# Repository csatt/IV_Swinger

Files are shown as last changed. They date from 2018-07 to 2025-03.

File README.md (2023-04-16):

# IV_Swinger

**NOTICE: Please contact me at csatt1@gmail.com if you are interested in building the hardware for people who don't have the time, skills, or tools to do it themselves. I get requests occasionally from such people, but cannot do this myself. There are now PCBs, making the construction much easier!**

The IV Swinger is an IV curve tracer for photovoltaic solar panels. Both the hardware design and the software are open source.

This GitHub repository contains the IV Swinger documentation, software, and open source licensing files.

IV Swinger 2 is here! It is much smaller, cheaper and easier to build, and better than the original in almost every way. Step-by-step construction instructions are included in the repository, and are posted on www.instructables.com:

[IV Swinger 2 - a $50 IV Curve Tracer](http://www.instructables.com/id/IV-Swinger-2-a-50-IV-Curve-Tracer/)

All IV Swinger 2 documentation is now available:
* IV Swinger 2: User Guide
* IV Swinger 2: Optional Environmental Sensors
* IV Swinger 2: Hardware Scaling
* IV Swinger 2: Design and Theory of Operation
* IV Swinger 2: Step-by-step Construction (for each variant)
* Fritzing files
* PCB schematics
* Bills of materials (BOMs) for each variant

YouTube demo videos (IV Swinger 2):

IV Swinger 2 Demo: Part I (http://www.youtube.com/watch?v=WhnTWciiNNo)

IV Swinger 2 Demo: Part II (http://www.youtube.com/watch?v=9iPq5AsuU_U)

YouTube demo video (original IV Swinger):

IV Swinger Demo (http://www.youtube.com/watch?v=xNytkONOcW0)

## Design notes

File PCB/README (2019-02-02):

This folder contains subfolders for each different type of IV Swinger
PCB.  Each subfolder contains an EAGLE subfolder with the schematic and
board files created with the free version of EAGLE.  There is also a
Gerber subfolder with the manufacturing files (in a zip archive) and a
PDF subfolder with PDFs of the schematic and images of the top and
bottom of the PCB.

All PCBs are Arduino "shields" that replace the PermaProto board in the
original IV Swinger 2 design.  They plug onto the top of the Arduino.
All are 2-layer boards.

IV_Swinger_2_module
-------------------
  This is the version for PV modules that requires an external
  electromechanical relay (EMR) module, just like the original. The only
  external wiring is between one screw-terminal block on the PCB and the
  relay module and between another screw-terminal block and the binding
  posts.  Additional external wires are required for the optional
  temperature and irradiance sensors.

  RevB
  ----
  Based on RevB of the SSR-based module version. The main purpose of
  this revision is to make the SSR and EMR versions as similar as
  possible, namely:

     - the connections to the binding posts are both on a screw-terminal
       block on the left end of the board (like SSR version)

     - pads are provided for the bypass diodes (like SSR version)

     - the current-carrying path from the shunt is now isolated in a
       stub off the ground plane (like SSR version)

     - R3 is now connected to the shunt with a dedicated trace (like SSR
       version)

     - Connections to EMR are from a second screw-terminal block that is
       located on the board where the SSRs are in the SSR version

  Note that there is nothing "wrong", per se, with the RevA board. This
  just cleans a few things up and makes it much easier to compare it
  with the SSR version.
  
  Status:   Verified
  To order: Submit Gerber files to www.pcbway.com

  RevA
  ----
  Status: OBSOLETE (but bug-free)

IV_Swinger_2_cell
-----------------
  This is similar to the IV_Swinger_2_module Arduino shield, but it is
  for use with PV cells.

  RevA
  ----
  Status:   Verified
  To order: Submit Gerber files to www.pcbway.com

IV_Swinger_2_ss_mod
-------------------
  This is similar to the IV_Swinger_2_module Arduino shield, but it uses
  three solid-state relays (SSRs) instead of the one electromechanical
  relay (EMR) module.  The only off-board connections are to the PV
  module itself (PV- and PV+). These can go to binding posts, or can be
  connected directly to wires with MC-4 connectors on their ends.

  RevB
  ----
  Status: Verified

  To order: Submit Gerber files to www.pcbway.com

  RevA
  ----
  Status: OBSOLETE (bugs: Issue #40, Issue #41; not viable)

IV_Swinger_2_ss_cell
--------------------
  This is similar to the IV_Swinger_2_ss_mod Arduino shield, but it is
  for use with PV cells.  It requires four SSRs.

  RevB
  ----
  Status:   Verified
  To order: Submit Gerber files to www.pcbway.com

  RevA
  ----
  Status:   OBSOLETE (bug: Issue #49, rework possible)

--------------------------------------------------------------------------------

Advantages of EMR designs:
  - EMR module is inexpensive (~$2), vs three/four SSRs (~$21/$28)
  - "Clicks" tell you it's working
  - EMR module is easy to replace if it goes bad
  
Advantages of SSR designs:
  - On-board:
     - No wires
     - No relay module to mount
  - Rated at 100V
  - No mechanical wearout
  - Silent

NOTE: The IV Swinger 2 Arduino code and application software work with
      all four variants.

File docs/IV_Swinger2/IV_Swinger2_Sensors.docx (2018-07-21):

# IV Swinger 2

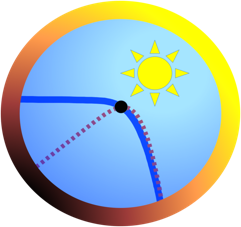
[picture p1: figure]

Optional Environmental Sensors

Document Revision: 1.00 (20-Jul, 2018) Chris Satterlee

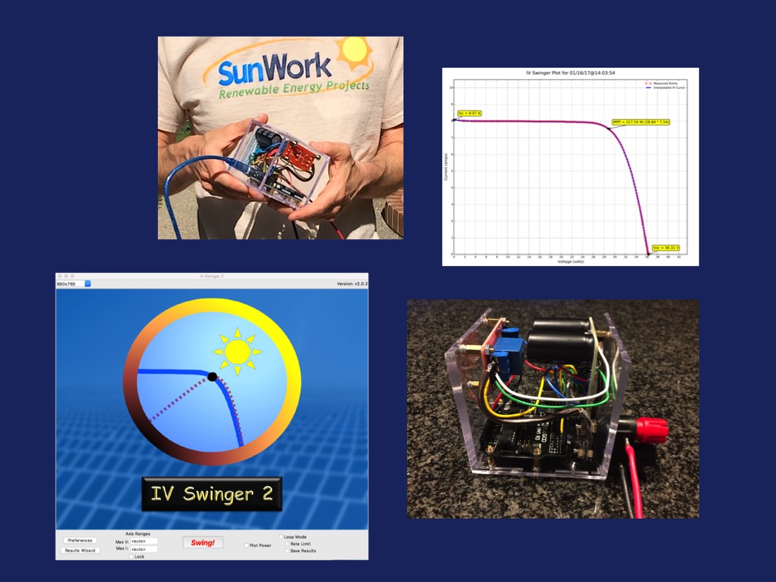
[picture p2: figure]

Copyright (C) 2018 Chris Satterlee

IV Swinger and IV Swinger 2 are open source hardware and software projects.

Permission to use the hardware design is granted under the terms of the TAPR Open Hardware License Version 1.0 (May 25, 2007) - http://www.tapr.org/OHL

Permission to use the software is granted under the terms of the GNU General Public License v3 - http://www.gnu.org/licenses.

Current versions of the license files, documentation, Fritzing file (hardware description), and software can be found at:

https://github.com/csatt/IV_Swinger

Table of Figures

# 1 Introduction

This document describes how to build and add optional environmental sensors to the IV Swinger 2 curve tracer.

As of this first writing, the only supported sensors are DS18B20 temperature sensors. However, the hope is eventually also to add support for an inexpensive DIY irradiance sensor (pyranometer).

# 2 DS18B20 Temperature Sensors

The DS18B20 is an inexpensive temperature sensor that can be purchased for less than $2 on Amazon, eBay, and other places. It comes in a TO-92-3 package that looks just like a discrete transistor as seen in Figure 2-1 below.

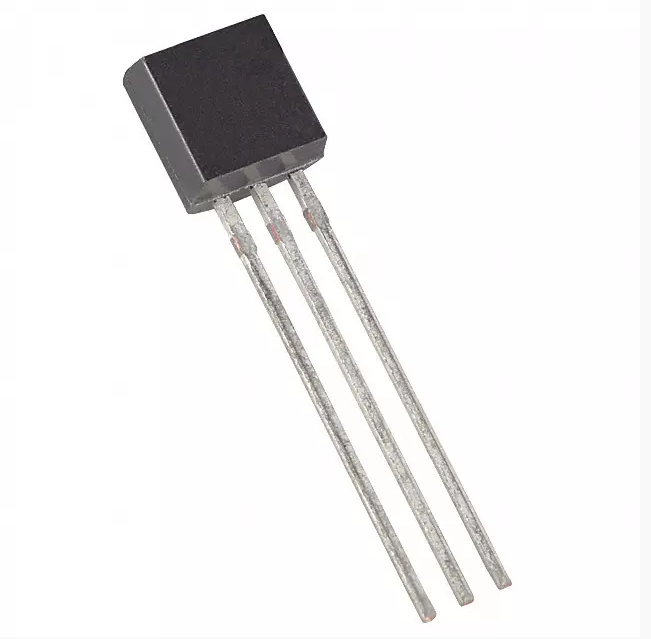
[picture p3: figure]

Figure 2-1: DS18B20 Sensor

It may also be purchased encapsulated in a waterproof enclosure with a 1-meter, 2-meter or 3-meter cable for not much more money than the device alone. These are abundant on Amazon and eBay. See Figure 2-2 below.

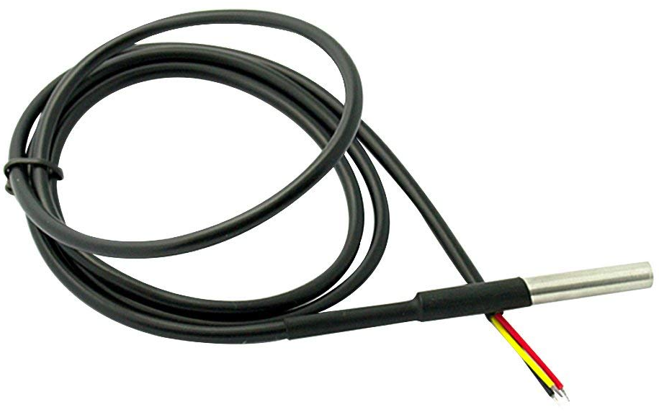
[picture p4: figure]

Figure 2-2: DS18B20 Waterproof Probe with Cable

In addition to being inexpensive and readily available, the DS18B20 has the following desirable characteristics:

- Only one Arduino signal pin is needed
- Multiple temperature sensors may be connected to the same one-wire interface
- Arduino library code is available
- Accuracy is more than adequate

## Connections

### Connecting One DS18B20 to IV Swinger 2

The connections that must be made in order for one DS18B20 to be detected and its temperature read by the IV Swinger 2 software are shown in Figure 2-3 below.

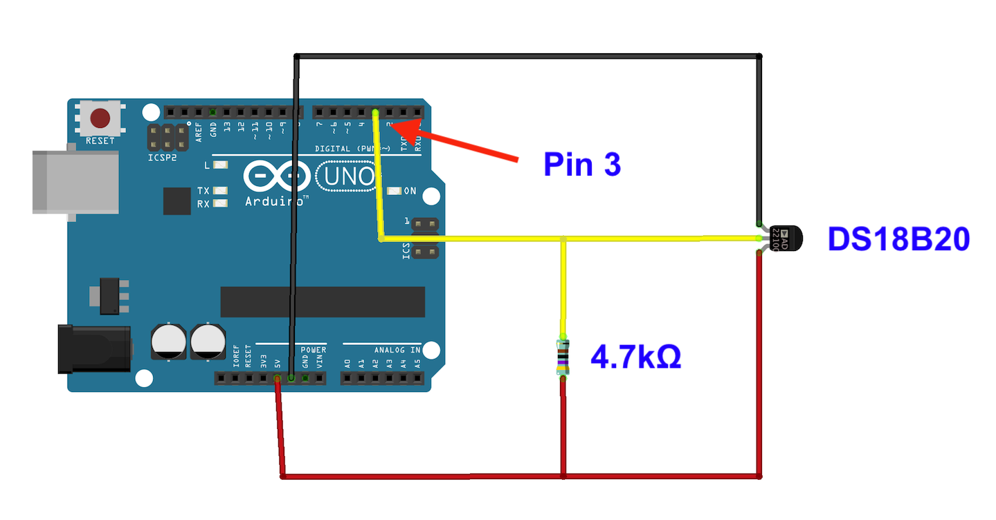
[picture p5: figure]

Figure 2-3: Connections for a Single DS18B20

The data (yellow) wire must connect directly to Pin 3 on the Arduino.

The power (red) wire can connect anywhere that is connected to the +5V pin on the Arduino, e.g. it can be soldered to the +5V rail on the PermaProto board. Optionally, it may be connected to the +3.3V pin on the Arduino.

The ground (black) wire can connect anywhere that is connected to the GND pin(s) on the Arduino, e.g. it can be soldered to the ground rail on the PermaProto board. Or it can connect directly to the unused GND pin on the Arduino itself.

The 4.7kΩ resistor must be connected between the data (yellow) wire and the power (red) wire. This resistor may be soldered to the PermaProto board, but that is not necessary. If you are adding the DS18B20 to an already-built IV Swinger 2, it will be easier to just solder this resistor to the two wires themselves – just make sure it is protected from shorting to anything (electrical tape, shrink tubing, etc.).

### Connecting Multiple DS18B20s to IV Swinger 2

A nice feature of the DS18B20 is that each one has a unique ROM code, which allows multiple sensors to be connected to the same data wire. The software can identify which sensor is which, and read each of their temperatures. This could be useful if you want to measure the temperature at multiple places on the module, for example.

Figure 2-4 below shows the addition of a second DS18B20.

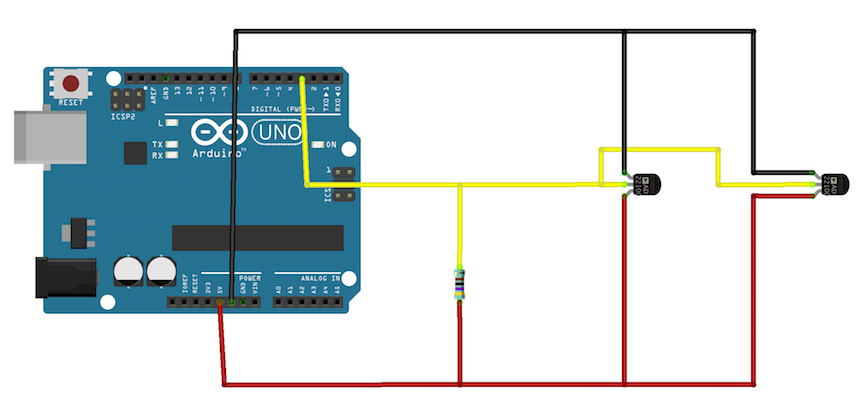
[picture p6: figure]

Figure 2-4: Connecting Additional DS18B20s

Note that there is only one 4.7kΩ resistor regardless of how many DS18B20s there are.

## Software Installation

The latest releases of the IV Swinger 2 Arduino sketch and laptop application have support for the DS18B20. However, the Arduino sketch makes use of the OneWire and DallasTemperature libraries, which must be installed. Also, the IV_Swinger2.ino file must be edited to uncomment one line.

### Installing Arduino Libraries

Two Arduino libraries must be installed:

- OneWire
- DallasTemperature

To do this from the Arduino IDE, use Sketch->Include Library->Manage Libraries…

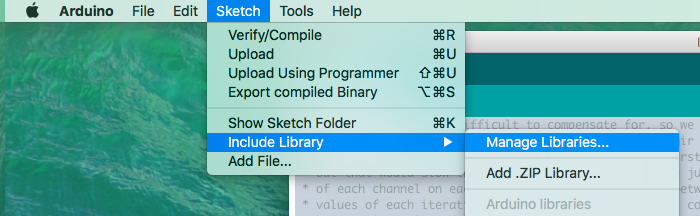
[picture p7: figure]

Search for “OneWire”. Click on the one with the name “OneWire” and then click on the Install button.

Search for “DallasTemperature”. Click on the one with the name “DallasTemperature” and then click on the Install button.

### Modifying IV_Swinger2.ino

Since temperature sensing is an optional feature, it was decided not to burden all users with having to install the OneWire and DallasTemperature libraries. The tradeoff is that users who do want to use this feature need to modify one line in the IV Swinger2 Arduino sketch.

You must manually change (“uncomment”) this line in IV_Swinger2.ino:

//#define DS18B20_SUPPORTED

to:

#define DS18B20_SUPPORTED

You may make this change using any text editor before starting up the Arduino IDE, or you may use the editor built into the Arduino IDE. If you have installed the OneWire and DallasTemperature libraries, the sketch should upload without errors.

Note that running code with this line uncommented will work fine even if there are no DS18B20s connected.

## Swinging IV Curves with Temperature Sensors

When you have one or more DS18B20s connected as described in Section 2.1 above and you have uploaded IV_Swinger2.ino with #define DS18B20_SUPPORTED uncommented, you don’t need to do anything else to get temperature readings.

### Temperature Scale

Temperatures are reported in degrees Celsius. There is no option to report in degrees Fahrenheit.

### Precision

Temperatures are reported in increments of 0.25˚C. The DS18B20 supports programmable precisions from 9 to 12 bits, and this is 10-bit precision. 12-bit precision readings take 3/4 second for each device, which is too slow. 10-bit readings take less than 1/4 second. This is currently hardcoded in the Arduino sketch, and there are no plans to make it configurable.

### Where Are the Temperatures recorded?

The laptop application records the temperature(s) in a “sensor info” file (which will also contain values from other environmental sensors if they exist). There is a sensor info file saved for each run and it is saved in the same directory/folder as the CSV, PDF and other files for the run.

The temperature or temperatures are also included on the graph itself, in the legend. Here is an example with two temperature sensors:

Each curve on an overlay will have the temperature(s) for that run:

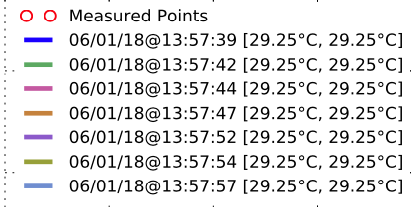
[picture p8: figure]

If you have only one sensor, that is all the information you need. But if you have more than one, you need to know which temperature is from which sensor. The File menu in the laptop application has an entry, “View Sensor Info File”:

The contents of the sensor info file might look like:

The ROM codes uniquely identify each sensor, but that is unlikely to be of much help. Probably the best way to identify which sensor is which is to use freeze spray, an ice cube, cold drink, or something like that to artificially cool one sensor at a time to see which one it is. Fortunately, the sensors will always be in the same order, so you only have to go through this identification process once.

The temperatures recorded in the legend entries on the graph are listed in order [#1, #2, …]

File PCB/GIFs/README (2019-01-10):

This folder contains GIFs that can be used to visually compare the
different PCB variants.

Schematics
----------
emr_mod_vs_ssr_mod_sch.gif:
   IV_Swinger_2_module compared with IV_Swinger_2_ss_mod
   
emr_mod_vs_emr_cell_sch.gif:
   IV_Swinger_2_module compared with IV_Swinger_2_cell
   
emr_cell_vs_ssr_cell_sch.gif:
   IV_Swinger_2_cell compared with IV_Swinger_2_ss_cell
   
ssr_mod_vs_ssr_cell_sch.gif:
   IV_Swinger_2_ss_mod compared with IV_Swinger_2_ss_cell
   
all_sch.gif:
   All four schematics

Board top/bottom
----------------
emr_mod_vs_ssr_mod_top.gif:
emr_mod_vs_ssr_mod_bot.gif:
   IV_Swinger_2_module compared with IV_Swinger_2_ss_mod
   
emr_mod_vs_emr_cell_top.gif:
emr_mod_vs_emr_cell_bot.gif:
   IV_Swinger_2_module compared with IV_Swinger_2_cell
   
emr_cell_vs_ssr_cell_top.gif:
emr_cell_vs_ssr_cell_bot.gif:
   IV_Swinger_2_cell compared with IV_Swinger_2_ss_cell
   
ssr_mod_vs_ssr_cell_top.gif:
ssr_mod_vs_ssr_cell_bot.gif:
   IV_Swinger_2_ss_mod compared with IV_Swinger_2_ss_cell

Bill of Materials
-----------------
emr_mod_vs_ssr_mod_BOM.gif:
   IV_Swinger_2_module compared with IV_Swinger_2_ss_mod
   
emr_mod_vs_emr_cell_BOM.gif:
   IV_Swinger_2_module compared with IV_Swinger_2_cell
   
emr_cell_vs_ssr_cell_BOM.gif:
   IV_Swinger_2_cell compared with IV_Swinger_2_ss_cell
   
ssr_mod_vs_ssr_cell_BOM.gif:
   IV_Swinger_2_ss_mod compared with IV_Swinger_2_ss_cell

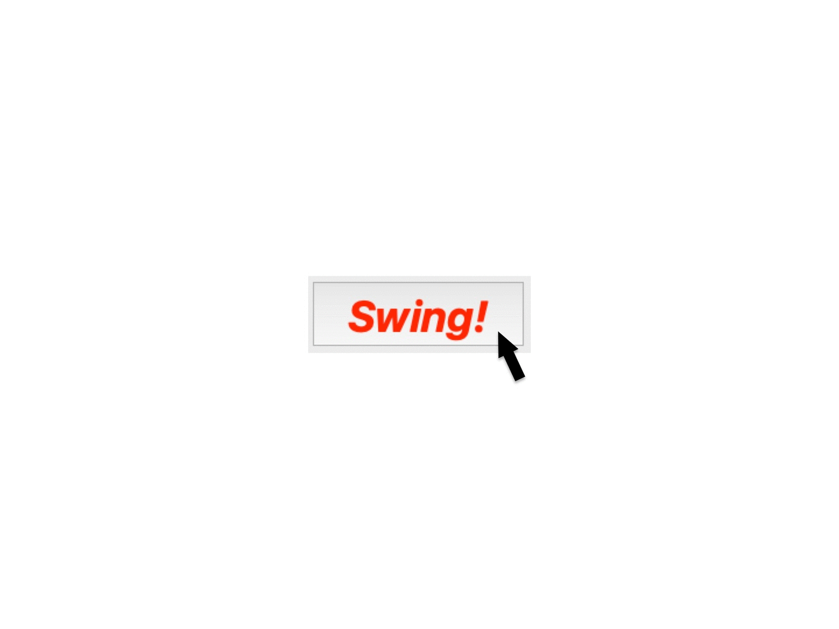
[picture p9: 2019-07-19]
docs/IV_Swinger2/Module_SSR_animation.gif

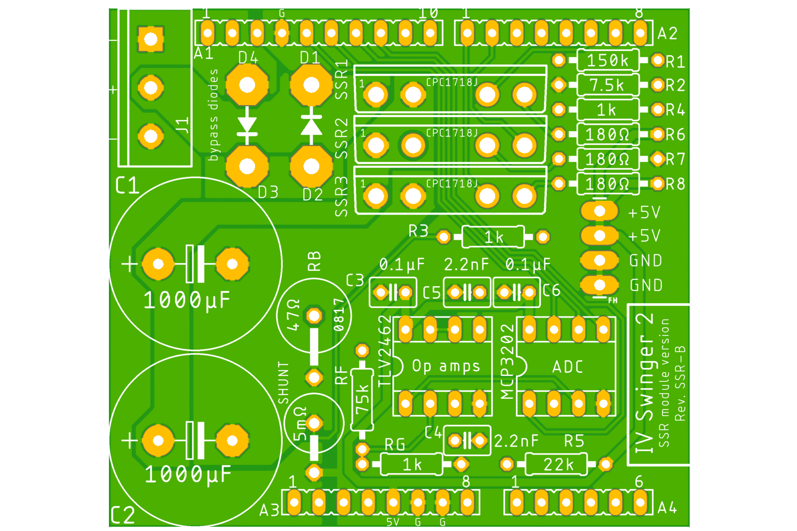
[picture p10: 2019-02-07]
PCB/GIFs/ssr_mod_vs_ssr_cell_top.gif

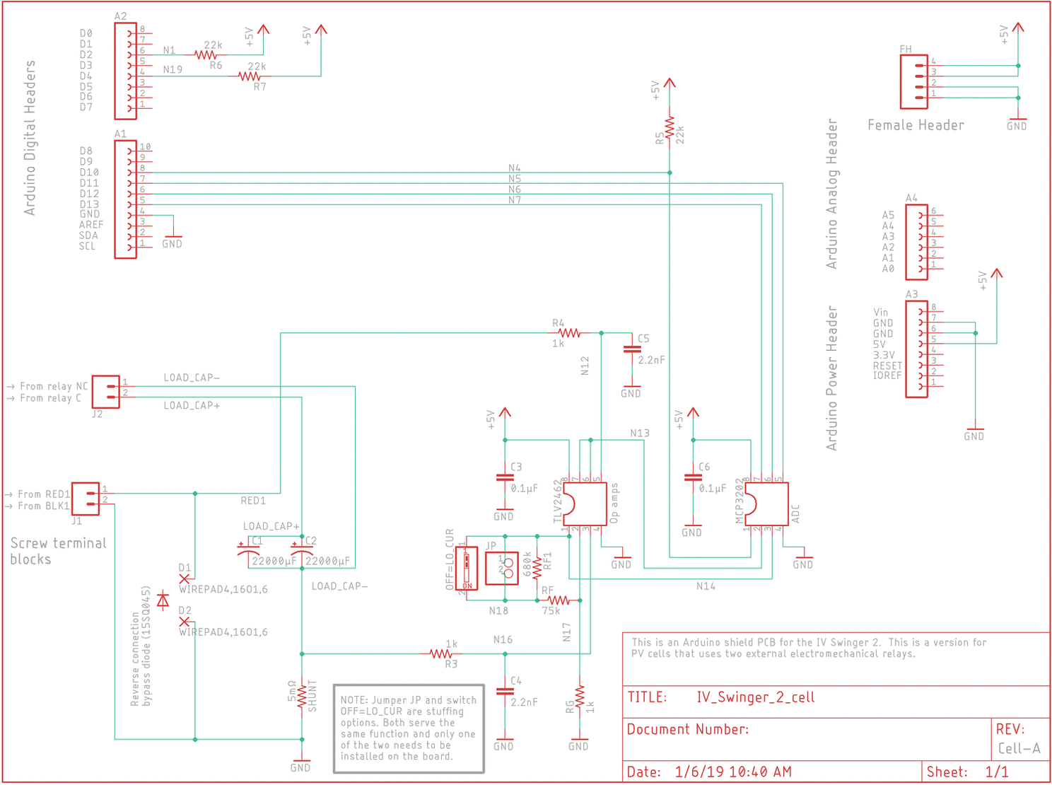
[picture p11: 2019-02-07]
PCB/GIFs/emr_cell_vs_ssr_cell_sch.gif

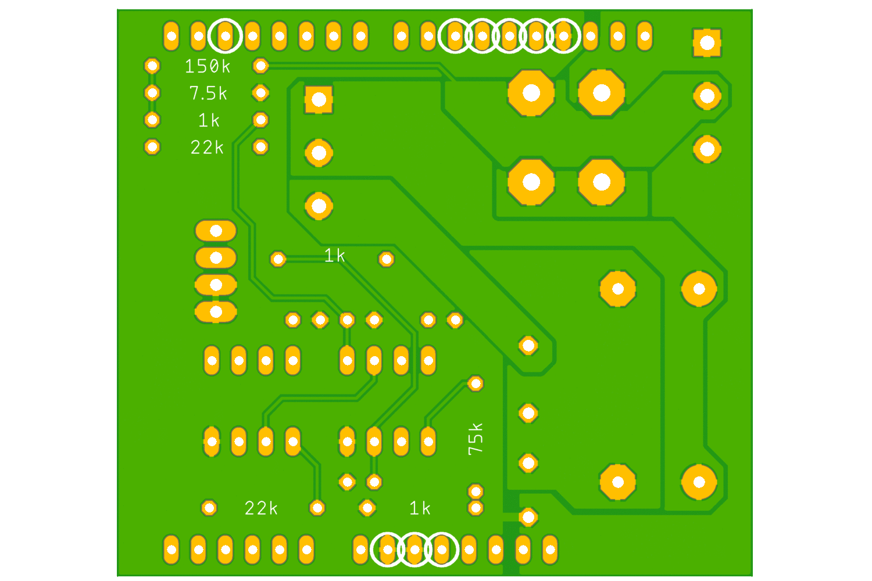
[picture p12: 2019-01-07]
PCB/GIFs/emr_mod_vs_ssr_mod_bot.gif

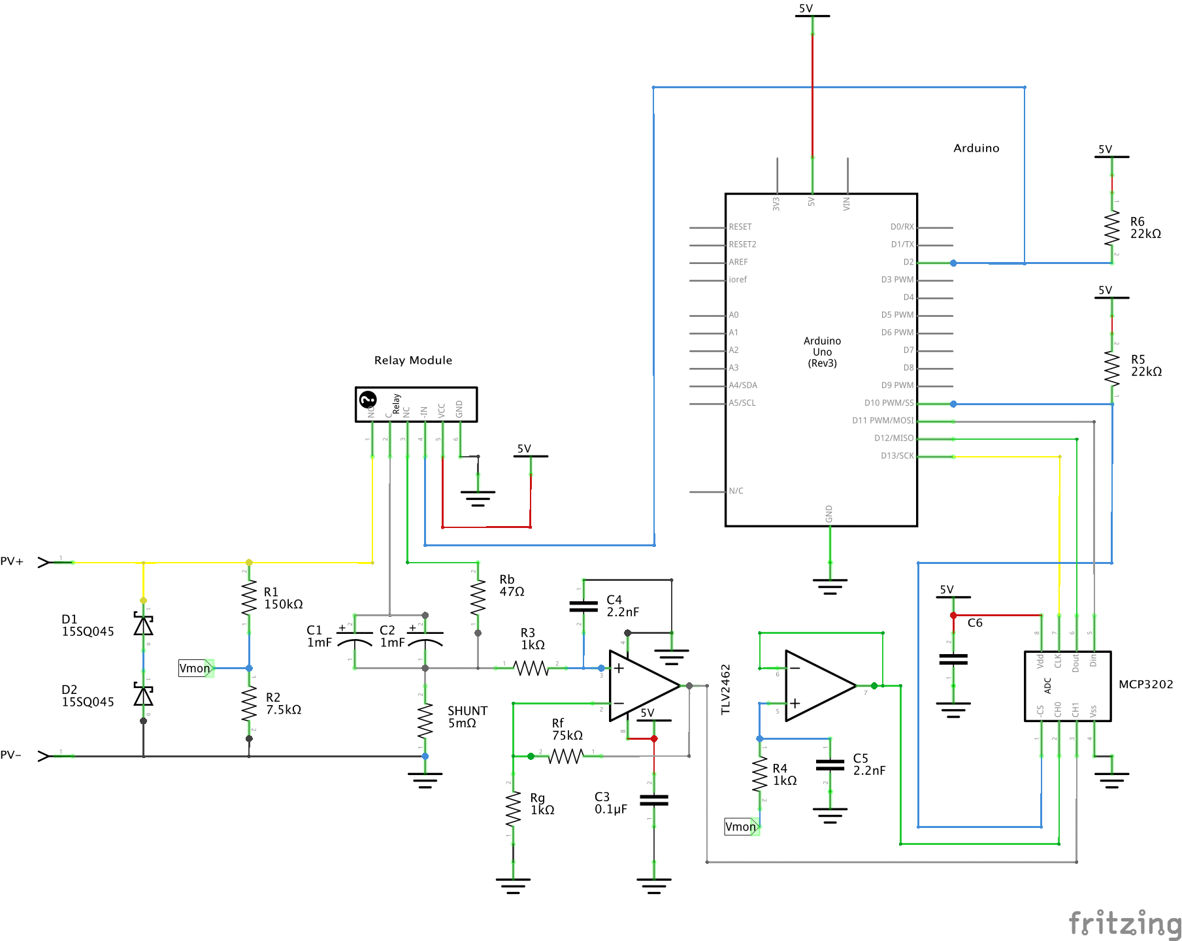
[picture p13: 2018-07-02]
Fritzing/Module_vs_Cell_schem.gif

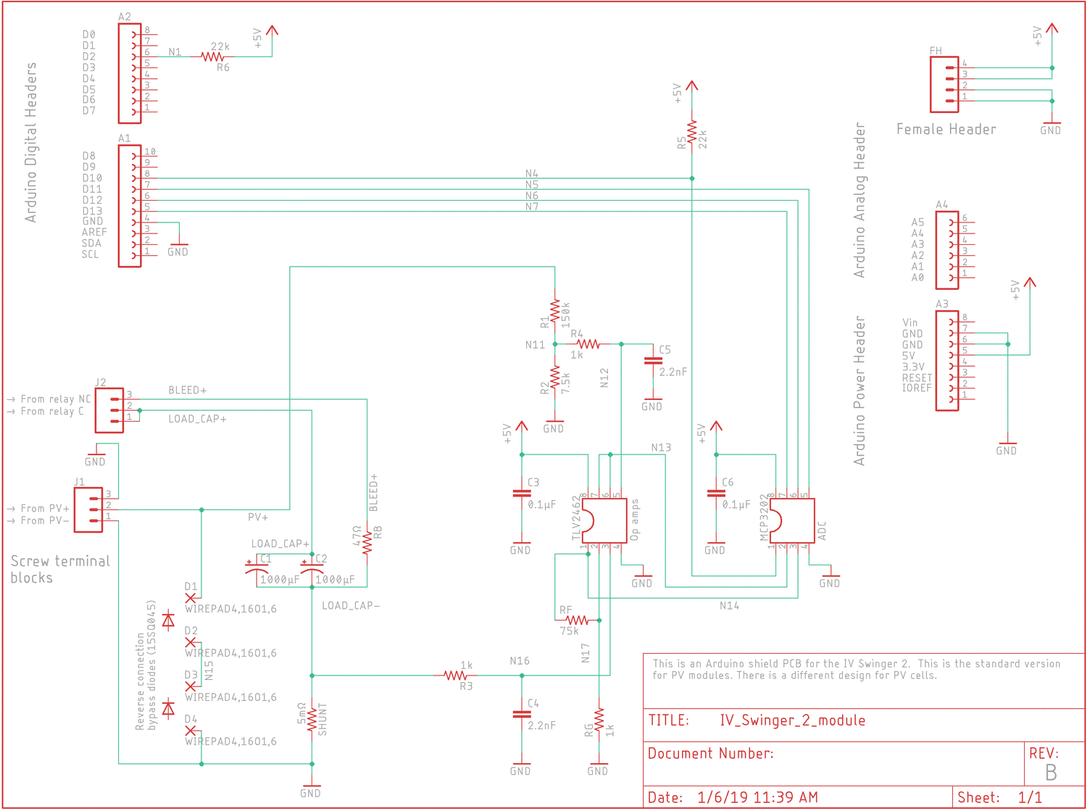
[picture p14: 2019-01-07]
PCB/GIFs/emr_mod_vs_emr_cell_sch.gif

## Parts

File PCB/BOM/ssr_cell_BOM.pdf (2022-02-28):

## PV type

## Relay Type

PV cell | SSR
Description | Quantity | Name(s) | Unit Price | Total Price | Purchase
From | Notes
10-pin stackable female header | 1 | A1 | $1.50 | $1.50 | Digi-Key | Purchased as a kit of all four. Note, however, that A4 is not needed. Digi-Key PN: 1568-1413-ND
8-pin stackable female header | 2 | A2, A3
6-pin stackable female header | 0 | A4
22000µF 6.3V capacitors | 2 | C1, C2 | $2.55 | $5.10 | Digi-Key | Digi-Key PN: 493-12454-ND
0.1µF capacitor | 2 | C3, C6 | $0.26 | $0.52 | Digi-Key | Op amp and ADC Vdd filter. Digi-Key PN: BC2665CT-ND
2.2nF (2200 pF) capacitor | 2 | C4, C5 | $0.38 | $0.76 | Digi-Key | Voltmeter and ammeter op amp circuits. Digi-Key PN: 399-4166-ND
4-pin female header | 1 | FH | $0.47 | $0.47 | Digi-Key | Extra +5V and GND for temperature and irradiance sensors. Can be omitted if no plans for those (or can be added later). Digi-Key PN: S7037-ND
2-pin screw-terminal block | 2 | J1, J2 | $0.99 | $1.98 | Digi-Key | Digi-Key PN: A97996-ND
8-pin DIP socket (optional) | 2 | MCP3202, TLV2462 | $0.45 | $0.90 | Digi-Key | IC sockets. Recommended so ICs can be replaced more easily. Digi-Key PN: 1212-1003-ND
ADC - MCP3202 | 1 | MCP3202 | $3.77 | $3.77 | Digi-Key | Digi-Key PN: MCP3202-BI/P-ND
Op amp – TLV2462 | 1 | TLV2462 | $2.82 | $2.82 | Digi-Key | Ammeter. Digi-Key PN: 296-1892-5-ND
Not present in cell version | 0 | R1 | $0.01 | $0.00 | Amazon | Voltmeter - divider
Not present in cell version | 0 | R2 | $0.01 | $0.00 | Amazon | Voltmeter - divider
1kΩ resistor - 1/4W | 3 | R3, R4, RG | $0.01 | $0.02 | Amazon | Voltmeter and ammeter op amp circuits, relay input
22kΩ resistor - 1/4W | 1 | R5 | $0.01 | $0.01 | Amazon | Arduino output pull-ups
180Ω resistor - 1/4W | 4 | R6, R9, R10, R11 | $0.01 | $0.03 | Amazon | SSR pull up/downs
75kΩ resistor - 1/4W | 1 | RF | $0.01 | $0.01 | Amazon | Ammeter - op amp circuit
680kΩ resistor - 1/4W | 1 | RF1 | $0.01 | $0.01 | Amazon | Ammeter - op amp circuit
Not present in cell version | 0 | RB | $0.78 | $0.00 | Digi-Key | Bleed resistor. Needs to be able to handle 6.4J pulse energy (for 80V Voc; less for lower Voc: 0.5 * 0.002F * Voc^2). Digi-Key PN:PPC5W47.0CT-ND
0.005Ω shunt resistor | 1 | SHUNT | $3.04 | $3.04 | Digi-Key | Ammeter. Digi-Key PN: 13FR005E-ND
2-pin header | 1 | JP | $0.13 | $0.13 | Digi-Key | Low current jumper header. Digi-Key PN: 732-5315-ND
2-pin jumper | 1 | JP | $0.10 | $0.10 | Digi-Key | Low current jumper. Digi-Key PN: S9337-ND
x1 DIP switch | 1 | OFF=LO_CUR | $0.91 | $0.91 | Digi-Key | Alternate to jumper. Digi-Key PN: 732-3831-5-ND
CPC1718J | 4 | SSR1, SSR4, SSR5, SSR6 | $7.00 | $28.00 | Digi-Key | Solid State Relays (SSRs). Digi-Key PN: CLA315-ND
Not present in EMR or SSR version | 0 | FET1, FET2, FET3 | $1.23 | $0.00 | Digi-Key | Field Effect Transistors (FETs). Digi-Key PN:IRF540NPBF-ND
Not present in EMR or SSR version | 0 | CPC1596 | $2.78 | $0.00 | Digi-Key | Gate driver for FET1. DigiKey PN:212-CPC1596G-ND
15SQ045 Schottky bypass diode(45V) | 1 | D1,D2 | $0.80 | $0.80 | Digi-Key | Reverse connection bypass diode. Connect between pads D1 and D2. Digi-Key PN: 1655-1354-1-ND
Arduino Uno clone | 1 | Arduino | $14.99 | $14.99 | Amazon | Elegoo UNO R3 Board ATmega328P ATMEGA16U2 with USB Cable Compatible With Arduino UNO R3
Donation to arduino.cc | 1 | Donation | $5.00 | $5.00 | arduino.cc
Binding posts | 2 | Binding posts | $4.09 | $8.18 | Digi-Key | Digi-Key PN: 501-1713-ND
Not present in SSR or FET version | 0 | EMR | $6.79 | $0.00 | Amazon | SunFounder 2 Channel DC 5V Relay Module with Optocoupler Low Level Trigger Expansion Board for Arduino UNO R3 MEGA 2560 1280 DSP ARM PIC AVR STM32 Raspberry Pi
18ga solid wire or zip cord | 1 | Load circuit wire | $2.94 | $2.94 | Amazon | For load circuit wires: MC-4 to binding posts, binding posts to PCB. Scrap appliance cord is fine. Just want a heavier duty than hookup wire.
Cable ring connectors | 4 | Cable rings | $0.21 | $0.84 | Digi-Key | Binding post internal connections. Digi-Key PN: 277-11154-ND
Not present in SSR or FET version | 0 | Jumpers | $0.07 | $0.00 | Amazon | Relay to stack connector wires. GenBasic 80 Piece Male to Female Solderless Ribbon Dupont Jumper Wires (4 and 8 Inch) for Breadboard Prototyping
Ultra Pro Baseball Clear Square Holder | 1 | Case | $5.99 | $5.99 | Amazon | Price goes up in baseball season
M3 15mm body, 6mm thread nylon male-female standoff spacer | 4 | Standoffs | $0.24 | $0.95 | Amazon | uxcell 50pcs M3 15+6mm Male Female Thread Nylon Hex Standoff Spacer Screws PCB Pillar Black (also available from Digi-Key or eBay)
M3 screws (1/4 inch) | 4 | Screws | $0.07 | $0.26 | Amazon | StarTech PC Mounting Computer Screws M3 x 1/4-Inches Long Standoff - 50 Pack SCREWM3 (also available from Digi-Key or eBay)
M3 nuts | 4 | Nuts | $0.06 | $0.25 | Amazon | Shapenty 100PCS 3mm Small Stainless Steel Female Thread Hex Screw Nut Fastener Tool, M3 (also available from Digi-Key or eBay)
Not needed for cell version | 0 | MC-4 | $4.99 | $0.00 | Amazon | JYFT Solar Panel Cable Connectors Male/Female IP67 30A 1000V DC (1Pair)
D-cell battery holders | 2 | $3.14 | $6.28 | Digi-Key | Digi-Key PN: BH2DL-ND
4-pack of D-cells | 1 | $7.98 | $7.98 | Amazon | Or at grocery store, Target, etc.
Total | | | $90.28

# Amazon wish list: http://a.co/cGEBoCO

Digi-Key cart: https://www.digikey.com/short/9r854mh9 Only purchase items with ALT_# in Customer Reference if

## primary has Availability = "Backorder"

Digi-Key/Mouser CSV: https://raw.githubusercontent.com/csatt/IV_Swinger/master/PCB/BOM/DigiKeyMouser/ssr_cell_DigiKey_Mouser.csv

## Bias Battery

# Bill of Materials for PCB-based IV Swinger 2

## On-PCB parts

## Off-PCB parts

## Enclosure

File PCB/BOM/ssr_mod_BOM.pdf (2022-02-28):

## PV type

## Relay Type

PV module | SSR
Description | Quantity | Name(s) | Unit Price | Total Price | Purchase
From | Notes
10-pin stackable female header | 1 | A1 | $1.50 | $1.50 | Digi-Key | Purchased as a kit of all four. Note, however, that A4 is not needed at all, and A1 can be 8-pin instead of 10-pin (pins 9 and 10 are not used). Digi-Key PN: 1568-1413-ND
8-pin stackable female header | 2 | A2, A3
6-pin stackable female header | 0 | A4
1000µF 100V capacitors | 2 | C1, C2 | $3.77 | $7.54 | Digi-Key | Digi-Key PN: 1572-1313-ND
0.1µF capacitor | 2 | C3, C6 | $0.26 | $0.52 | Digi-Key | Op amp and ADC Vdd filter. Digi-Key PN: BC2665CT-ND
2.2nF (2200 pF) capacitor | 2 | C4, C5 | $0.38 | $0.76 | Digi-Key | Voltmeter and ammeter op amp circuits. Digi-Key PN: 399-4166-ND
4-pin female header | 1 | FH | $0.47 | $0.47 | Digi-Key | Extra +5V and GND for temperature and irradiance sensors. Can be omitted if no plans for those (or can be added later). Digi-Key PN: S7037-ND
2-pin screw-terminal block | 1 | J1 | $0.99 | $0.99 | Digi-Key | Digi-Key PN: A97996-ND
8-pin DIP socket (optional) | 2 | MCP3202, TLV2462 | $0.45 | $0.90 | Digi-Key | IC sockets. Recommended so ICs can be replaced more easily. Digi-Key PN: 1212-1003-ND
ADC - MCP3202 | 1 | MCP3202 | $3.77 | $3.77 | Digi-Key | Digi-Key PN: MCP3202-BI/P-ND
Op amp – TLV2462 | 1 | TLV2462 | $2.82 | $2.82 | Digi-Key | Ammeter. Digi-Key PN: 296-1892-5-ND
150kΩ resistor - 1/4W | 1 | R1 | $0.01 | $0.01 | Amazon | Voltmeter - divider
7.5kΩ resistor - 1/4W | 1 | R2 | $0.01 | $0.01 | Amazon | Voltmeter - divider
1kΩ resistor - 1/4W | 3 | R3, R4, RG | $0.01 | $0.02 | Amazon | Voltmeter and ammeter op amp circuits, relay input
22kΩ resistor - 1/4W | 1 | R5 | $0.01 | $0.01 | Amazon | Arduino output pull-ups
180Ω resistor - 1/4W | 3 | R6, R7, R8 | $0.01 | $0.02 | Amazon | SSR pull up/downs
75kΩ resistor - 1/4W | 1 | RF | $0.01 | $0.01 | Amazon | Ammeter - op amp circuit
Not present in module version | 0 | RF1 | $0.01 | $0.00 | Amazon | Ammeter - op amp circuit
47Ω 5W resistor | 1 | RB | $0.78 | $0.78 | Digi-Key | Bleed resistor. Needs to be able to handle 6.4J pulse energy (for 80V Voc; less for lower Voc: 0.5 * 0.002F * Voc^2). Digi-Key PN:PPC5W47.0CT-ND
0.005Ω shunt resistor | 1 | SHUNT | $3.04 | $3.04 | Digi-Key | Ammeter. Digi-Key PN: 13FR005E-ND
Not present in module version | 0 | JP | $0.13 | $0.00 | Digi-Key | Low current jumper header. Digi-Key PN: 732-5315-ND
Not present in module version | 0 | JP | $0.10 | $0.00 | Digi-Key | Low current jumper. Digi-Key PN: S9337-ND
Not present in module version | 0 | OFF=LO_CUR | $0.91 | $0.00 | Digi-Key | Alternate to jumper. Digi-Key PN: 732-3831-5-ND
CPC1718J | 3 | SSR1, SSR2, SSR3 | $7.00 | $21.00 | Digi-Key | Solid State Relays (SSRs). Digi-Key PN: CLA315-ND
Not present in EMR or SSR version | 0 | FET1, FET2, FET3 | $1.23 | $0.00 | Digi-Key | Field Effect Transistors (FETs). Digi-Key PN:IRF540NPBF-ND
Not present in EMR or SSR version | 0 | CPC1596 | $2.78 | $0.00 | Digi-Key | Gate driver for FET1. DigiKey PN:212-CPC1596G-ND
15SQ100 Schottky bypass diode (100V) | 1 | D1,D4 | $0.84 | $0.84 | Digi-Key | Reverse connection bypass diode. Connect between pads D1 and D4. Digi-Key PN: 1655-1355-1-ND
Arduino Uno clone | 1 | Arduino | $14.99 | $14.99 | Amazon | Elegoo UNO R3 Board ATmega328P ATMEGA16U2 with USB Cable Compatible With Arduino UNO R3
Donation to arduino.cc | 1 | Donation | $5.00 | $5.00 | arduino.cc
Binding posts | 1 | Binding posts | $4.09 | $4.09 | Digi-Key | Digi-Key PN: 501-1713-ND
Not present in SSR or FET version | 0 | EMR | $1.80 | $0.00 | Amazon | 5V 1 Channel Relay Shield Module Optocoupler For PIC AVR DSP ARM Arduino TE213
18ga solid wire or zip cord | 1 | Load circuit wire | $2.94 | $2.94 | Amazon | For load circuit wires: MC-4 to binding posts, binding posts to PCB. Scrap appliance cord is fine. Just want a heavier duty than hookup wire.
Cable ring connectors | 2 | Cable rings | $0.21 | $0.42 | Digi-Key | Binding post internal connections. Digi-Key PN: 277-11154-ND
Not present in SSR or FET version | 0 | Jumpers | $0.07 | $0.00 | Amazon | Relay to stack connector wires. GenBasic 80 Piece Male to Female Solderless Ribbon Dupont Jumper Wires (4 and 8 Inch) for Breadboard Prototyping
Ultra Pro Baseball Clear Square Holder | 1 | Case | $5.99 | $5.99 | Amazon | Price goes up in baseball season
M3 15mm body, 6mm thread nylon male-female standoff spacer | 4 | Standoffs | $0.24 | $0.95 | Amazon | uxcell 50pcs M3 15+6mm Male Female Thread Nylon Hex Standoff Spacer Screws PCB Pillar Black (also available from Digi-Key or eBay)
M3 screws (1/4 inch) | 4 | Screws | $0.07 | $0.26 | Amazon | StarTech PC Mounting Computer Screws M3 x 1/4-Inches Long Standoff - 50 Pack SCREWM3 (also available from Digi-Key or eBay)
M3 nuts | 4 | Nuts | $0.06 | $0.25 | Amazon | Shapenty 100PCS 3mm Small Stainless Steel Female Thread Hex Screw Nut Fastener Tool, M3 (also available from Digi-Key or eBay)
MC-4 connector (male/female pair) | 1 | MC-4 | $4.99 | $4.99 | Amazon | JYFT Solar Panel Cable Connectors Male/Female IP67 30A 1000V DC (1Pair)
Not present in module version | 0 | $3.14 | $0.00 | Digi-Key | Digi-Key PN: BH2DL-ND
Not present in module version | 0 | $7.98 | $0.00 | Amazon | Or at grocery store, Target, etc.
Total | | | $84.89

# Amazon wish list: http://a.co/gWW20Gs

Digi-Key cart: https://www.digikey.com/short/87v1995h Only purchase items with ALT_# in Customer Reference if

## primary has Availability = "Backorder"

Digi-Key/Mouser CSV: https://raw.githubusercontent.com/csatt/IV_Swinger/master/PCB/BOM/DigiKeyMouser/ssr_mod_DigiKey_Mouser.csv

## Bias Battery

# Bill of Materials for PCB-based IV Swinger 2

## On-PCB parts

## Off-PCB parts

## Enclosure

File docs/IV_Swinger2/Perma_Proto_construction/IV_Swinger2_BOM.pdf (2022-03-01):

Description | Quantity | Unit Price | Total Price | Purchased From | Notes
Binding posts | 1 | $4.09 | $4.09 | Digi-Key | Digi-Key PN: 501-1713-ND
Relay module | 1 | $1.80 | $1.80 | Amazon | 5V 1 Channel Relay Shield Module Optocoupler For PIC AVR DSP ARM Arduino TE213
1000µF 100V capacitors | 2 | $3.77 | $7.54 | Digi-Key | Digi-Key PN: 1572-1313-ND
MC-4 connector (male/female pair) | 1 | $4.99 | $4.99 | Amazon | JYFT Solar Panel Cable Connectors Male/Female IP67 30A 1000V DC (1Pair)
47Ω 5W resistor | 1 | $0.78 | $0.78 | Digi-Key | Bleed resistor. Needs to be able to handle 6.4J pulse energy (for 80V Voc; less for lower Voc: 0.5 * 0.002F * Voc^2). Digi-Key PN:PPC5W47.0CT-ND
18ga solid wire or zip cord, 3ft | 1 | $2.94 | $2.94 | Amazon | For load circuit wires: MC-4 to binding posts, PV+ binding post to relay, PV- binding post to Perma-Proto, relay to Perma-Proto. Scrap appliance cord is fine. Just want a heavier duty than hookup wire.
15SQ100 Schottky bypass diode | 1 | $0.84 | $0.84 | Digi-Key | Reverse connection bypass diode. Connect between binding posts. Digi-Key PN: 1655-1355-1-ND
Cable ring connectors | 2 | $0.18 | $0.36 | Digi-Key | Binding post internal connections. Digi-Key PN: 277-11154-ND
ADC - MCP3202 | 1 | $3.77 | $3.77 | Digi-Key | Digi-Key PN: MCP3202-BI/P-ND
Op amp – TLV2462 | 1 | $2.82 | $2.82 | Digi-Key | Ammeter. Digi-Key PN: 296-1892-5-ND
0.005Ω shunt resistor | 1 | $3.04 | $3.04 | Digi-Key | Ammeter. Digi-Key PN: LVRB-.005RCT-ND
0.1µF capacitor | 2 | $0.26 | $0.52 | Digi-Key | Op amp and ADC Vdd filter. Digi-Key PN: BC2665CT-ND
8-pin DIP socket (optional) | 2 | $0.45 | $0.90 | Digi-Key | IC sockets. Recommended so ICs can be replaced more easily. Digi-Key PN: 1212-1003-ND
150kΩ resistor - 1/4W | 1 | $0.01 | $0.01 | Amazon | Voltmeter - divider
7.5kΩ resistor - 1/4W | 1 | $0.01 | $0.01 | Amazon | Voltmeter - divider
75kΩ resistor - 1/4W | 1 | $0.01 | $0.01 | Amazon | Ammeter - op amp circuit
1kΩ resistor - 1/4W | 3 | $0.01 | $0.02 | Amazon | Voltmeter and ammeter op amp circuits, relay input
22kΩ resistor - 1/4W | 2 | $0.01 | $0.01 | Amazon | Arduino output pull-ups
2.2nF (2200 pF) capacitor | 2 | $0.04 | $0.09 | Amazon | Voltmeter and ammeter op amp circuits
Arduino Uno clone | 1 | $14.99 | $14.99 | Amazon | Elegoo UNO R3 Board ATmega328P ATMEGA16U2 with USB Cable Compatible With Arduino UNO R3
Donation to arduino.cc | 1 | $5.00 | $5.00 | arduino.cc
Adafruit Perma-Proto half-size breadboard | 1 | $4.50 | $4.50 | Digi-Key | Digi-Key PN: 1528-1195-ND
22 AWG solid core hookup wire - 6 colors - 25' each | 5 | $0.18 | $0.88 | Amazon | Elenco Solid Hook-Up Wire Kit 6 Colors in a dispenser box # WK-106
4" Male to Female jumpers (1 blue, 1 red, 1 black) | 3 | $0.07 | $0.22 | Amazon | GenBasic 80 Piece Male to Female Solderless Ribbon Dupont Jumper Wires (4 and 8 Inch) for Breadboard Prototyping
StarTech PC Mounting Computer Screws M3 x 1/4-Inches Long Standoff - 50 Pack SCREWM3 | 10 | $0.08 | $0.78 | Amazon | 1 per standoff
M3 nuts | 10 | $0.06 | $0.63 | Amazon | 1 per standoff
uxcell 20pcs M3 8+6mm Female Male Thread Brass Hex Standoff Spacer Screws PCB Pillar | 10 | $0.30 | $3.00 | Amazon | Standoffs
Ultra Pro Baseball Clear Square Holder | 1 | $5.99 | $5.99 | Amazon
Total | $70.52 | Was under $50 in 2017

# Amazon wish list: http://a.co/8RzkH2P

# Digi-Key cart: https://www.digikey.com/short/q99cnzz1

## Only purchase items with ALT_# in Customer Reference if primary has Availability = "Backorder"

Digi-Key/Mouser CSV: https://raw.githubusercontent.com/csatt/IV_Swinger/master/docs/IV_Swinger2/Perma_Proto_construction/PermaProto_Digikey_Mouser.csv

## Load circuit

## Meters

## Enclosure

## Computer and Electronics

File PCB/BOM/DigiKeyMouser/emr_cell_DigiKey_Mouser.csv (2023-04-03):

Quantity | Mfg | Mfg Part Number | Digi-Key Part Number | Mouser Part Number | Customer Reference | Notes
1 | Microchip Technology | MCP3202-BI/P | MCP3202-BI/P-ND | 579-MCP3202-BI/P | MCP3202 | ADC
1 | Texas Instruments | TLV2462CP | 296-1892-5-ND | 595-TLV2462CP | TLV2462 | Op amps
2 | Cornell Dubilier | 108CKS100MRY | 493-12454-ND | 598-108CKS100MRY | C1_C2 | Load capacitors
2 | Vishay | K104K10X7RF5UH5 | BC2665CT-ND | 594-K104K10X7RF5UH5 | C3_C6
2 | KEMET | C315C222K1R5TA | 399-4166-ND | N/A | C4_C5
1 | Vishay | AC05000004709JAC00 | PPC5W47.0CT-ND | 594-AC05W47R00J | RB | Bleed resistor
1 | Ohmite | 13FR005E | 13FR005E-ND | 588-13FR005E | SHUNT
1 | SMC Diode Solutions | 15SQ100TR | 1655-1354-1-ND | N/A | 45V_DIODE | Bypass diode
2 | Preci-dip | 110-87-304-41-001101 | 1212-1003-ND | 437-1108730441001101 | DIP_SOCKET | Also available on Amazon list (qty 60)
1 | SparkFun Electronics | PRT-11417 | 1568-1413-ND | 474-PRT-11417 | A1_A2_A3_A4 | Stacking headers
2 | Pomona Electronics | 6884 | 501-1713-ND | 565-6884 | BINDING POSTS
1 | Sullins Connector Solutions | PPPC041LFBN-RC | S7037-ND | N/A | FH | Alt: can cut A4 and trim pins
2 | TE Connectivity | 1776244-2 | A97996-ND | 571-1776244-2 | J1_J2
4 | Phoenix Contact | 3240080 | 277-11154-ND | 651-3240080 | CABLE RING CONNECTORS | Not needed if solid wire is used
8 | Essentra | CBMFTS270A | RPC3006-ND | 144-CBMFTS270A | STANDOFFS | Also available on Amazon list (qty 50)
1 | Wurth Elektronik | 61300211121 | 732-5315-ND | 710-61300211121 | JP_HEADER
1 | Sullins Connector Solutions | QPC02SXGN-RC | S9337-ND | N/A | JP_JUMPER
1 | Wurth Elektronik | 418117270901_ | 732-3831-5-ND | 710-418117270901 | OFF=LO_CUR
2 | MPD (Memory Protection Devices) | BH2DL_ | BH2DL-ND | N/A | BIAS BATTERY HOLDER
1 | Adafruit | 85 | 1528-1074-ND | 485-85 | ALT_1 A1_A2_A3_A4 | Stacking headers
2 | Mueller Electric | BU-P6883 | 314-1549-ND | 548-BU-P6883 | ALT_1 BINDING POSTS
2 | KEMET | C315C222K1R5TA7303 | 399-14037-1-ND | 80-C315C222K1R5TATU | ALT_1 C4_C5
1 | Microchip Technology | MCP3202-CI/P | MCP3202-CI/P-ND | 579-MCP3202-CI/P | ALT_1 MCP3202 | ADC
1 | TE Connectivity | 534237-2 | A26416-ND | 571-5342372 | ALT_1 FH
1 | Vishay | AC05AT0004709JAC00 | 749-1863-1-ND | 594-AC05AT0004709JAC | ALT_1 RB | Bleed resistor
1 | Riedon | MT2B-0R005F1 | 696-1733-ND | N/A | ALT_1 SHUNT
1 | Texas Instruments | TLV2462IP | 296-1893-5-ND | 595-TLV2462IP | ALT_1 TLV2462 | Op amps
2 | CLIFF Electronic Components Ltd | CL159706PA | 3185-CL159706PA-ND | N/A | ALT_2 BINDING POSTS
2 | Kyocera AVX | SR201A222JAA | 478-11700-ND | 581-SR201A222J | ALT_2 C4_C5
1 | TE Connectivity | SQPW547RJ | A137443-ND | 279-SQPW547RJ | ALT_2 RB | Bleed resistor
1 | Ohmite | 15FR005E | 15FR005E-ND | 588-15FR005E | ALT_2 SHUNT
2 | CLIFF Electronic Components Ltd | CL159706PB | 3185-CL159706PB-ND | N/A | ALT_3 BINDING POSTS
1 | Ohmite | 12FR005E | 12FR005E-ND | 588-12FR005E | ALT_3 SHUNT

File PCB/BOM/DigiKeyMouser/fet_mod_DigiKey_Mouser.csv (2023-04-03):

Quantity | Mfg | Mfg Part Number | Digi-Key Part Number | Mouser Part Number | Customer Reference | Notes
3 | Infineon | IRF540NPBF | IRF540NPBF-ND | 942-IRF540NPBF | FET1_FET2_FET3 | FETs
1 | IXYS | CPC1596G | 212-CPC1596G-ND | 849-CPC1596G | CPC1596 | FET gate driver
1 | Microchip Technology | MCP3202-BI/P | MCP3202-BI/P-ND | 579-MCP3202-BI/P | MCP3202 | ADC
1 | Texas Instruments | TLV2462CP | 296-1892-5-ND | 595-TLV2462CP | TLV2462 | Op amps
2 | Cornell Dubilier | 108CKS100MRY | 1572-1313-ND | 598-108CKS100MRY | C1_C2 | Load capacitors
2 | Vishay | K104K10X7RF5UH5 | BC2665CT-ND | 594-K104K10X7RF5UH5 | C3_C6
2 | KEMET | C315C222K1R5TA | 399-4166-ND | N/A | C4_C5
1 | Vishay | AC05000004709JAC00 | PPC5W47.0CT-ND | 594-AC05W47R00J | RB | Bleed resistor
1 | Ohmite | 13FR005E | 13FR005E-ND | 588-13FR005E | SHUNT
1 | SMC Diode Solutions | 15SQ100TR | 1655-1355-1-ND | N/A | 100V_DIODE | Bypass diode
2 | Preci-dip | 110-87-304-41-001101 | 1212-1003-ND | 437-1108730441001101 | DIP_SOCKET | Also available on Amazon list (qty 60)
1 | SparkFun Electronics | PRT-11417 | 1568-1413-ND | 474-PRT-11417 | A1_A2_A3_A4 | Stacking headers
1 | Pomona Electronics | 6884 | 501-1713-ND | 565-6884 | BINDING POSTS
1 | Sullins Connector Solutions | PPPC041LFBN-RC | S7037-ND | N/A | FH | Alt: can cut A4 and trim pins
1 | TE Connectivity | 1776244-2 | A97996-ND | 571-1776244-2 | J1
2 | Phoenix Contact | 3240080 | 277-11154-ND | 651-3240080 | CABLE RING CONNECTORS | Not needed if solid wire is used
4 | Essentra | CBMFTS270A | RPC3006-ND | 144-CBMFTS270A | STANDOFFS | Also available on Amazon list (qty 50)
1 | Adafruit | 85 | 1528-1074-ND | 485-85 | ALT_1 A1_A2_A3_A4 | Stacking headers
1 | Mueller Electric | BU-P6883 | 314-1549-ND | 548-BU-P6883 | ALT_1 BINDING POSTS
2 | KEMET | C315C222K1R5TA7303 | 399-14037-1-ND | 80-C315C222K1R5TATU | ALT_1 C4_C5
3 | Infineon | IRF540NLPBF | IRF540NLPBF-ND | 942-IRF540NLPBF | ALT_1 FET1_FET2_FET3 | FETs
1 | Microchip Technology | MCP3202-CI/P | MCP3202-CI/P-ND | 579-MCP3202-CI/P | ALT_1 MCP3202 | ADC
1 | TE Connectivity | 534237-2 | A26416-ND | 571-5342372 | ALT_1 FH
1 | Vishay | AC05AT0004709JAC00 | 749-1863-1-ND | 594-AC05AT0004709JAC | ALT_1 RB | Bleed resistor
1 | Riedon | MT2B-0R005F1 | 696-1733-ND | N/A | ALT_1 SHUNT
1 | Texas Instruments | TLV2462IP | 296-1893-5-ND | 595-TLV2462IP | ALT_1 TLV2462 | Op amps
1 | SMC Diode Solutions | 12TQ100 | 1655-1001-ND | N/A | ALT_1 100V_DIODE | Bypass diode
1 | CLIFF Electronic Components Ltd | CL159706PA | 3185-CL159706PA-ND | N/A | ALT_2 BINDING POSTS
2 | Kyocera AVX | SR201A222JAA | 478-11700-ND | 581-SR201A222J | ALT_2 C4_C5
1 | TE Connectivity | SQPW547RJ | A137443-ND | 279-SQPW547RJ | ALT_2 RB | Bleed resistor
1 | Ohmite | 15FR005E | 15FR005E-ND | 588-15FR005E | ALT_2 SHUNT
1 | SMC Diode Solutions | 12TQ150 | 1655-1002-ND | N/A | ALT_2 100V_DIODE | Bypass diode
1 | CLIFF Electronic Components Ltd | CL159706PB | 3185-CL159706PB-ND | N/A | ALT_3 BINDING POSTS
1 | Ohmite | 12FR005E | 12FR005E-ND | 588-12FR005E | ALT_3 SHUNT
1 | SMC Diode Solutions | 12TQ200 | 1655-1003-ND | N/A | ALT_3 100V_DIODE | Bypass diode

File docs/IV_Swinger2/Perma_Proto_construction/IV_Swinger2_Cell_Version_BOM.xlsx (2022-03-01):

NOTE: The prices and other details below are out of date. The PermaProto based cell version IVS2 is deprecated. The PCB-based cell versions are somewhat supported, but in reality no one has built them, so they are effectively deprecated too.
Description | Quantity | Unit Price | Total Price | Purchased From | Notes
Load circuit
Binding posts | 2 | $2.67 | $5.34 | Digi-Key | Digi-Key PN: 501-1713-ND | need two for cell version
Dual Relay Module | 1 | $7.99 | $7.99 | Amazon | 5V Two 2 Channel Relay Module With optocoupler Compatible With Arduino PIC AVR DSP ARM | could also use two single modules, but then each has its own power and ground
22000µF 6.3V capacitors | 2 | $3.49 | $6.98 | Digi-Key | Digi-Key PN: 565-4042-ND | take the place of 1000µF, 100V caps in module IVS2
MC-4 connector (male/female pair) | 0 | $1.40 | $0.00 | Amazon | Sun YOBA 5 Pairs of MC4 Male/ Female Solar Panel Cable Connectors | not needed for cell version
47Ω 5W resistor | 0 | $0.78 | $0.00 | Digi-Key | Bleed resistor. Needs to be able to handle 6.4J pulse energy (for 80V Voc; less for lower Voc: 0.5 * 0.002F * Voc^2). Digi-Key PN:PPC5W47.0CT-ND | just a wire (0Ω resistor) in cell version
18ga solid wire or zip cord, 3ft | 1 | $0.96 | $0.96 | Amazon | For load circuit wires: MC-4 to binding posts, PV+ binding post to relay, PV- binding post to Perma-Proto, relay to Perma-Proto. Scrap appliance cord is fine. Just want a heavier duty than hookup wire. | low resistance is MORE important in cell version!
15SQ045 Schottky bypass diodes | 1 | $0.44 | $0.44 | Amazon | EFF-cientt 20pcs 15amp Diode Axial Schottky Blocking Diodes for Solar Cells Panel,15SQ045 Schottky | only need one because voltage is lower
Cable ring connectors | 2 | $0.18 | $0.36 | Digi-Key | Binding post internal connections. Digi-Key PN: 277-11154-ND
Meters
ADC - MCP3202 | 1 | $2.98 | $2.98 | Digi-Key | Digi-Key PN: MCP3202-BI/P-ND
Op amp – TLV2462 | 1 | $2.58 | $2.58 | Digi-Key | Ammeter. Digi-Key PN: 296-1892-5-ND
0.005Ω shunt resistor | 1 | $2.05 | $2.05 | Digi-Key | Ammeter. Digi-Key PN: LVRB-.005RCT-ND
0.1µF capacitor | 2 | $0.18 | $0.36 | Digi-Key | Op amp and ADC Vdd filter. Digi-Key PN: BC2665CT-ND
8-pin DIP socket (optional) | 2 | $0.12 | $0.25 | Amazon | uxcell 60 Pcs 8 Pin 2.54mm Pitch DIP IC Sockets Adaptor
150kΩ resistor - 1/4W | 1 | $0.01 | $0.01 | Amazon | Voltmeter - divider | no voltage divider in cell version
7.5kΩ resistor - 1/4W | 1 | $0.01 | $0.01 | Amazon | Voltmeter - divider | no voltage divider in cell version
75kΩ resistor - 1/4W | 1 | $0.01 | $0.01 | Amazon | Ammeter - op amp circuit
680kΩ resistor - 1/4W | 1 | $0.01 | $0.01 | Amazon | Ammeter - op amp circuit (Rf1) | for low-power mode
1kΩ resistor - 1/4W | 3 | $0.01 | $0.02 | Amazon | Voltmeter and ammeter op amp circuits, relay input
22kΩ resistor - 1/4W | 3 | $0.01 | $0.02 | Amazon | Arduino output pull-ups | need one more for 2nd relay
2.2nF (2200 pF) capacitor | 2 | $0.04 | $0.09 | Amazon | Voltmeter and ammeter op amp circuits
x1 DIP switch | 1 | $9.99 | $9.99 | Amazon | Haobase 35Pcs/Lot Dip Switch Kit In Box 1 2 3 4 5 6 8 Way 2.54mm Toggle Switch Red Snap Switches Kit( Each value 5Pcs)). Ammeter- Rf1 Bypass | for low-power mode; can't buy just one - this is a kit with many of different sizes
Computer and Electronics
Arduino Uno clone | 1 | $10.86 | $10.86 | Amazon | Elegoo UNO R3 Board ATmega328P ATMEGA16U2 with USB Cable Compatible With Arduino UNO R3
Donation to arduino.cc | 1 | $5.00 | $5.00 | arduino.cc
Adafruit Perma-Proto half-size breadboard | 1 | $4.50 | $4.50 | Digi-Key | Digi-Key PN: 1528-1195-ND
22 AWG solid core hookup wire - 6 colors - 25' each | 5 | $0.13 | $0.65 | Amazon | Elenco Solid Hook-Up Wire Kit 6 Colors in a dispenser box # WK-106
4" Male to Female jumpers (1 blue, 1 red, 1 black) | 3 | $0.07 | $0.22 | Amazon | GenBasic 80 Piece Male to Female Solderless Ribbon Dupont Jumper Wires (4 and 8 Inch) for Breadboard Prototyping
StarTech PC Mounting Computer Screws M3 x 1/4-Inches Long Standoff - 50 Pack SCREWM3 | 10 | $0.06 | $0.64 | Amazon | 1 per standoff
8mm Body Long M3 Male Female Brass Pillar Standoff Spacer 100Pcs | 10 | $0.05 | $0.55 | Amazon | Came with nuts - otherwise also need 10 M3 nuts
Enclosure
Ultra Pro Baseball Clear Square Holder | 1 | $5.20 | $5.20 | Amazon
Total |  |  | $68.07

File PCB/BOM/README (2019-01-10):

Bill of Materials
-----------------

There is a single configurable spreadsheet in this folder that serves as
the BOM for all four versions of the PCB:
  
     IV_Swinger_2_PCB_BOM.xlsx

Near the top are two cells containing RED text that specify the PV type
and relay type.  Each of these cells has a pull-down list that
constrains its values.

     PV type: "PV module" or "PV cell"

    Relay type: "EMR" or "SSR"

--------------------------------------------------------------------------------
PCB name                PV type       Relay type
--------                -------       ----------
IV_Swinger_2_module:    PV module     EMR
IV_Swinger_2_cell:      PV cell       EMR
IV_Swinger_2_ss_mod:    PV module     SSR
IV_Swinger_2_ss_cell:   PV cell       SSR
--------------------------------------------------------------------------------

The items in the BOM that are dependent on the PV type and/or the relay
type change based on the values in those two cells.  Items that are not
present at all for the given configuration are shown with a quantity of
0 and are grayed out.

This folder also contains PDFs generated for each of the four
configurations:

   emr_mod_BOM.pdf
   emr_cell_BOM.pdf
   ssr_mod_BOM.pdf
   ssr_cell_BOM.pdf

Additionally, in ../GIFs there are animations that do pairwise comparisons:

   ../GIFs/emr_mod_vs_emr_cell_BOM.gif
   ../GIFs/emr_mod_vs_ssr_mod_BOM.gif
   ../GIFs/ssr_mod_vs_ssr_cell_BOM.gif
   ../GIFs/emr_cell_vs_ssr_cell_BOM.gif

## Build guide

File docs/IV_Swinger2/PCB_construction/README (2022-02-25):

The original IV Swinger 2 designs (for PV modules and PV cells) use a
"Perma-Proto" board and hand-cut, hand-stripped, hand-soldered hookup
wires for all of the connections between the resistors, capacitors, ICs,
and power/ground rails.  Hookup wire is also used for the connections
between the Perma-Proto and the Arduino.

Now there are printed circuit boards (PCBs) available that provide all
of these connections, making the construction much simpler, faster, and
more mistake-proof.  Furthermore, there are versions of the PCBs that
support on-board solid-state relays (SSRs) or field-effect transistors
(FETs) instead of the off-board electromagnetic relays (EMRs).

It is recommended that, moving forward, all IV Swinger 2 constructions
use the PCB-based designs.

The legacy documentation that describes the construction of older
Perma-Proto-based designs is contained in the Perma_Proto folder. This
folder contains the documents that are specific to construction using
the PCBs.

There are five PCB variants:

    EMR-based version for PV modules
    SSR-based version for PV modules 
    FET-based version for PV modules 
    EMR-based version for PV cells 
    SSR-based version for PV cells

The step-by-step instructions for building the PCB-based IV Swinger 2
variants are contained in the variant-specific documents:

   IV_Swinger2_EMR_mod_PCB_Step_by_Step.docx
   IV_Swinger2_EMR_mod_PCB_Step_by_Step_v<x>.pdf
   IV_Swinger2_SSR_mod_PCB_Step_by_Step.docx
   IV_Swinger2_SSR_mod_PCB_Step_by_Step_v<x>.pdf
   IV_Swinger2_FET_mod_PCB_Step_by_Step.docx
   IV_Swinger2_FET_mod_PCB_Step_by_Step_v<x>.pdf
   IV_Swinger2_EMR_cell_PCB_Step_by_Step.docx
   IV_Swinger2_EMR_cell_PCB_Step_by_Step_v<x>.pdf
   IV_Swinger2_SSR_cell_PCB_Step_by_Step.docx
   IV_Swinger2_SSR_cell_PCB_Step_by_Step_v<x>.pdf

Drawings of the off-PCB connections are contained in the following:

   Off_PCB_Connections.pptx
   Off_PCB_Connections_v<x>.pdf

The bills-of-materials (BOMs) for the PCB designs are NOT in this
folder; they are in the IV_Swinger/PCB/BOM folder.  Note that these BOMs
contain the parts that are soldered onto the PCBs, but they also contain
all of the other parts needed to completely construct a PCB-based IV
Swinger 2.  However, they do not include the parts or instructions for
adding temperature and irradiance sensors (see the IV_Swinger2_Sensors
document for that).

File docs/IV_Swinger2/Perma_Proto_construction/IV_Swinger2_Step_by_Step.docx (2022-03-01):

# IV Swinger 2


Step-by-step Construction

Document Revision: 1.04 (03-Feb, 2022) Chris Satterlee

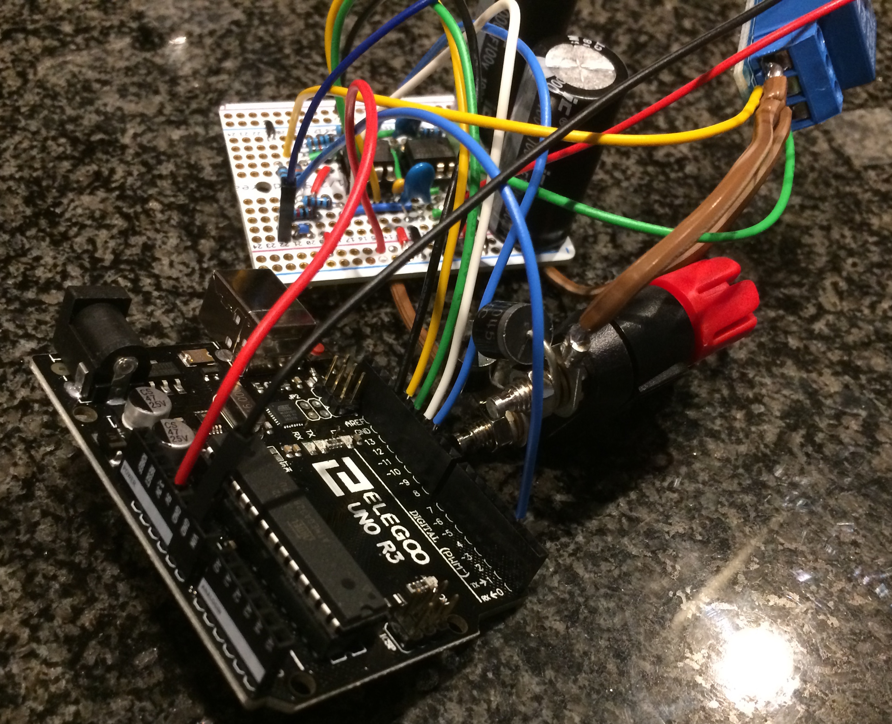
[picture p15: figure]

Copyright (C) 2017, 2019, 2022 Chris Satterlee

IV Swinger and IV Swinger 2 are open source hardware and software projects.

Permission to use the hardware design is granted under the terms of the TAPR Open Hardware License Version 1.0 (May 25, 2007) - http://www.tapr.org/OHL

Permission to use the software is granted under the terms of the GNU General Public License v3 - http://www.gnu.org/licenses.

Current versions of the license files, documentation, Fritzing file (hardware description), and software can be found at:

https://github.com/csatt/IV_Swinger

# Intro

IV Swinger 2 is an IV curve tracer for photovoltaic (PV) solar panels (modules). There is also a version that works with PV cells.

In 2017, the total cost of materials was about $50 (for the least expensive version) but may be more to build a single IV Swinger 2 since that assumes some items are purchased in larger quantities. It also does not include tools or the Windows/Mac laptop that is required to use it.

This is a successor to IV Swinger, which was used for Gil Masters' CEE176B class at Stanford in 2015 and 2016. IV Swinger 2 was used for that class from 2017 until Gil’s retirement in 2020. It is my sincere hope that IV Swinger 2 will be used at other colleges and universities that teach PV principles. For that matter, it can be very useful for anyone wanting to learn about the effects of insolation/irradiance, temperature, and especially shading on the power production of a single PV module. While the software does support calibration, there are no guarantees as to the device’s precision or accuracy.

The following two YouTube videos demonstrate IV Swinger 2 in action:

Part I: https://youtu.be/WhnTWciiNNo (7:02)

Part II: https://youtu.be/9iPq5AsuU_U (6:48)

The hardware and software designs and documentation for IV Swinger 2 (and the original IV Swinger) are on GitHub:

https://github.com/csatt/IV_Swinger

I also want to acknowledge Jason Alderman (whom I have never met or even corresponded with). I stumbled on his wireless IV curve tracer design (http://jalderman.org/?p=57), and that was the "Aha!" moment without which IV Swinger 2 might not have happened.

This document contains step-by-step instructions to build an IV Swinger 2.

The original IV Swinger 2 designs (for PV modules and PV cells) use an Adafruit "Perma-Proto" board and hand-cut, hand-stripped, hand-soldered hookup wires for all of the connections between the resistors, capacitors, ICs, and power/ground rails. Hookup wire is also used for the connections between the Perma-Proto and the Arduino.

Now there are printed circuit boards (PCBs) available that provide all of these connections, making the construction much simpler, faster, and more mistake-proof. Furthermore, there are versions of the PCBs that support on-board solid-state relays (SSRs) or field-effect transistors (FETs) instead of the off-board electromagnetic relays (EMRs).

It is still possible to build an IV Swinger 2 using a Perma-Proto; the documentation still exists and the software doesn’t care. However, it is recommended that moving forward, all IV Swinger 2 constructions use the PCB-based designs.

These are the same instructions that are on www.instructables.com but do not include any of the photos or videos. The purpose of this document is primarily so you can print it out and check off completed steps and make other notes as you work on the project. You should use the Instructable to take advantage of the visual aids:

https://www.instructables.com/id/IV-Swinger-2-a-50-IV-Curve-Tracer

# Step 1: Understand the HW design / Choose Variant

Understand the hardware design:

Although it is possible to build an IV Swinger 2 without understanding how the hardware works, you will get more out of it if you do and will have a better chance of being able to diagnose any problems.

The IV Swinger 2 hardware consists of the following:

- Load:
  - Capacitors
  - Bleed resistor
  - Relay
- Ammeter and voltmeter:
  - Shunt resistor
  - Voltage divider
  - Op amp circuits
- Arduino UNO

The following YouTube video gives a high-level description of how a capacitor load is used to trace an IV curve:

https://youtu.be/eTSCVlSTUP4 (6:00)

There are seven design variants.

Perma-Proto:

- PV module version, electromechanical relay (EMR)
- PV cell version, electromechanical relay (EMR)

PCB:

- PV module version, electromechanical relay (EMR)
- PV module version, solid-state relays (SSR)
- PV module version, field-effect transistors (FET)
- PV cell version, electromechanical relays (EMR)
- PV cell version, solid-state relays (SSR)

The GitHub repository (https://github.com/csatt/IV_Swinger) contains Fritzing design files for the Perma-Proto module and cell IV Swinger 2 designs. Images of the Breadboard View and Schematic View (module only) are attached to this step in the Instructable. The repository also contains the PCB designs that were created with the EAGLE tool (free version). Each PCB has a PDF folder that contains the schematic of the circuit design. These schematics are for the PCB only. Even if you are building a PCB-based IV Swinger 2, it is still useful to look at the schematic created with the Fritzing tool for the original design, since it includes the external components (Arduino, relay, binding posts) and it shows the internal op amps in the TLV2462 IC. The circuit design is described in detail in the document titled “IV Swinger 2: Design and Theory of Operation” (file name IV_Swinger2_Design.pdf), available in the GitHub repository under docs/IV_Swinger2.

Choose Variant:

Deciding which variant to build comes down to three choices:

- Perma-Proto vs PCB
- PV module vs PV cell
- EMR vs SSR vs FET

As mentioned earlier, it is recommended that from now on, everyone should choose PCB over Perma-Proto. This is especially true if you need to build the cell version, since there is no Instructable and no step-by-step instruction document for the Perma-Proto cell version.

If you need to trace IV curves for high-power PV cells, one of the cell versions must be chosen. You should know, however, that the cell versions:

- Are more expensive and difficult to build
- Require an external “bias battery”
- Are trickier to calibrate
- Are not necessary at all for low-power cells, which can be accommodated with a “scaled-down” module version (please read the document titled “IV Swinger 2: Hardware Scaling”, filename: IV_Swinger2_Scaling.pdf to determine whether your cells will work with a scaled module version and what component values to use to accomplish that.)

From an educational standpoint, more can be learned from IV curves for PV modules since they show the effects of module-level electronics (namely bypass diodes).

Choosing between the electromechanical relay (EMR) versions, solid-state relay (SSR) versions and field-effect transistor (FET) version comes down to:

- Cost: the EMR versions are the least expensive to build. The FET version (module only) is next, and the SSR versions are the most expensive.
- Availability: The EMR modules are very common and available from many sources. The SSRs are a very specific part that has been nearly impossible to find during the global semiconductor shortages of 2021 and 2022. The FET version was developed specifically to address the unavailability of the SSR parts, but also requires a part (CPC1596) that could encounter similar shortages.
- Simplicity: the SSR and FET versions have fewer external wires to connect and no EMR to mount in the case.
- High voltage tolerance: The SSR and FET versions can handle PV modules with a Voc up to 80 volts. The EMR version will wear out quickly at voltages over about 40V and may even burn out immediately with a Voc higher than some (unknown) voltage.
- Lifespan: An EMR has moving parts and will eventually wear out, even at lower voltages.
- Repairability: The EMR is easy to replace if it goes bad. The SSRs and FETs are difficult to replace (but shouldn’t go bad, so this point may be moot).
- Sound: An EMR clicks when it switches. This can be a nice audible cue that an IV curve was swung. The SSRs and FETs are silent.
- Isc accuracy: The first measurement that the SSR and FET versions capture is at a voltage closer to zero than the EMR version, so the (extrapolated) value of Isc is more accurate.
- Current calibration: The SSR and FET versions support an advanced method of calibrating the current measurements which is more accurate than the method for the EMR versions.
- Track record: the EMR and SSR versions have been built many times and are known to work well. The FET version is new (as of Feb 2022).

If cost isn’t a big concern, the SSR or FET versions are probably a better choice than the EMR versions.

The step-by-step construction documents for the PCB-based designs can be found in the GitHub repository:

docs/IV_Swinger2/PCB_construction/

IV_Swinger2_EMR_mod_PCB_Step_by_Step.docx
IV_Swinger2_SSR_mod_PCB_Step_by_Step.docx
IV_Swinger2_FET_mod_PCB_Step_by_Step.docx
IV_Swinger2_EMR_cell_PCB_Step_by_Step.docx
IV_Swinger2_SSR_cell_PCB_Step_by_Step.docx

PDFs of those documents are in the same place. Please switch now to the one that corresponds to your choice unless you have decided to build the original (deprecated) Perma-Proto design for PV modules.

The remainder of this document is for the original Perma-Proto design for PV modules.

# Step 2: Install software

Before spending time building the hardware, install the Arduino software and the IV Swinger 2 application on the laptop that you’ll be using.

- Install Arduino IDE:

https://www.arduino.cc/en/Main/Software

- Install IV Swinger 2 app:

https://github.com/csatt/IV_Swinger/releases

- Make sure both of the above come up before proceeding. If necessary, upgrade the OS on your computer

# Step 3: Buy parts

The necessary parts to build an IV Swinger 2 can all be purchased online from Amazon and Digi-Key.

The Amazon link below is a “wish list” that can be used to populate your cart. Most of the items come in quantities larger (in some cases much larger) than needed to build a single IV Swinger 2. You may of course choose to find equivalents that are offered in smaller quantities. Also, many of the items are things that you may already have, so don’t necessarily just blindly order everything on the list.

The Digi-Key link is a pre-populated shopping cart. Again, you’ll want to check if you already have any of the items before ordering. NOTE: any part that has ALT_n (e.g., ALT_1, ALT_2) in the “Customer Reference field should be ordered only if the primary version of the same part is marked as “backorder”.

In both cases, it is possible (or probable) that certain items will go out of stock or be discontinued, so you’ll have to find suitable substitutions. Occasionally I check the lists and modify them myself, but not very often. Send me a message if you are uncertain about identifying a substitute part.

Alternately, the following CSV file may be used to order from Digi-Key, Mouser or possibly other suppliers that support uploading a BOM spreadsheet. It includes the manufacturer, manufacturer’s part number, Digi-Key part number, and Mouser part number:

https://github.com/csatt/IV_Swinger/raw/master/PCB/BOM/DigiKeyMouser/PermaProto_Digikey_Mouser.csv

https://github.com/csatt/IV_Swinger/raw/master/PCB/BOM/DigiKeyMouser/PermaProto_Digikey_Mouser.csv

Also included below is the link to donate to the original Arduino developers. I donate $5 for each $10 Arduino clone that I buy. This is your choice, but I think it is the right thing to do.

- Amazon: http://a.co/8RzkH2P
- Digi-Key:

https://www.digikey.com/short/q99cnzz1

- Donate to Arduino.cc: https://www.arduino.cc/en/Main/Contribute

# Step 4: Gather / buy tools

- Holding:
  - Vise
  - 3rd hand tool with magnifying glass
  - Tape (preferably Kapton, but Scotch ok)
  - Long/needle-nosed pliers
- Soldering:
  - Soldering iron (preferably temp controlled solder station)
  - Tip cleaner
  - Rosin core solder
  - Solder sucker or solder wick
- Cutting:
  - Utility knife
  - Coping saw (or hacksaw)
  - Wire cutter (flush cut)
  - Wire stripper
- Drilling:
  - Drill
  - 1/16" bit (pilot for 9/64")
  - 1/8" bit (Perma-Proto)
  - 9/64" bit (standoffs)
  - 11/64" bit (pilot for 13/64")
  - 13/64" bit (binding posts)
  - 3/8" Forstner bit (preferred - USB cable hole)
- Other:
  - Digital Multimeter (DMM)
  - Small Phillips screwdriver
  - 9V battery
  - Sharpie
  - Ruler
  - Water spray bottle

# Step 5: Modify Perma-Proto

The 1/2-size Perma-Proto is just a bit too long to fit in the baseball display case.

- Cut Perma-Proto to length:
  - 6.5cm (cut between row 24 and 25) ___________
  - Score with knife on both sides, and then break off end
- Drill new mounting hole in cut-off end of Perma-Proto:
  - 1/8" bit, ~5.5cm between hole centers _________

# Step 6: Manually test the relay module

This will confirm that your relay module is the correct type and that it is functional.

  - With Arduino powered off:
    - Connect relay module GND to Arduino GND with female-to-male jumper ___________
    - Connect relay module VCC to Arduino 5V with female-to-male jumper ___________
    - Connect female-to-male jumper to relay module IN (male end not connected) ___________
  - Connect Arduino to laptop with USB cable:
    - Arduino: green LED should be on ___________
    - Arduino: yellow LED should be blinking once per second (assuming fresh-out-of box Arduino, running the default "Blink" sketch) ___________
    - Relay module: red LED should be on, green LED should be off ___________
    - Relay module: C (middle) terminal should have continuity with NC (bottom) terminal and no continuity with NO (top) terminal ___________
  - Connect the male end of the jumper from the relay module IN pin to the GND socket near the blinking yellow LED on the Arduino ___________
    - Relay module: should click and green LED should come on ___________
    - Relay module: C (middle) terminal should have continuity with NO (top) terminal and no continuity with NC (bottom) terminal ___________
  - Connect the male end of the jumper from the relay module IN pin to the "13" socket near the blinking yellow LED on the Arduino ___________
    - Relay module: should click once per second ___________
    - Relay module: green LED should blink exactly opposite from the Arduino's yellow LED ___________

# Step 7: Prepare for Soldering

- Soldering NOTES:
- Order is important:
- Avoids earlier steps obstructing later steps
- Avoids melting insulation of already-soldered wires
- Minimizes time by batching as many solder joints as possible into a single "step"
- If you don't have a lot of soldering experience, read this:

https://learn.adafruit.com/adafruit-guide-excellent-soldering/common-problems

- If you need practice soldering, use the scrap end of the Perma-Proto
- Solder bridges between holes in different numbered rows (e.g. hole 16H to hole 17H) or between the power and ground rails must be removed with a solder sucker or solder wick and/or X-acto knife.
- Solder bridges are ok between holes in the same numbered row (e.g. holes 10B and 10C). However, if an empty hole is plugged, it may block a wire/lead/pin that comes in a later step and will have to be cleared with a solder sucker or solder wick.
- Don't skip the incremental testing steps. Mistakes found now are easy to identify and fix, but will be very difficult or impossible if you wait until the whole thing is built.
- Wire cutting NOTES:
- Print the following page to help cut wires to their correct lengths and to strip them properly
- Measure #10 – it should be 38.0mm if your printer prints to scale
- The numbered templates are named for the number of hole gaps spanned for purely vertical or horizontal wires (e.g. adjacent holes use #1)
- The lettered templates are for a few wires that are diagonal or not routed directly between two holes
- To use:
- Lay the uncut wire over the template, with the end aligned to the right end of the template
- Use wire cutters to gently dent the insulation at the positions of the two ends of the insulation and the left end of the wire
- Use wire strippers to strip the right end at the rightmost dent
- Cut the wire to length at the leftmost dent
- Hold the wire by the insulation with needle nosed pliers
- Use wire strippers to strip the left end at the first dent
- Total counts for each color and length:
- BLACK:
  - #2: 2
  - #3: 4
  - #4: 2
- RED:
  - #2: 3
  - #A: 1
- BLUE:
  - #1: 1
  - #6: 1
- GREEN:
  - #1: 1
  - #B: 2
- WHITE:
  - #C: 1

Wire cutting and stripping templates

#C

#B

#A

#1010

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
#1 15

# Step 8: BLACK (ground) wires

- Solder BLACK (ground) wires to Perma-Proto (16 joints):
- Only the ones with both ends connecting to Perma-Proto holes
- Insert all wires before soldering. Tape down on front to hold in place. Lengths (total/insulation template#) and holes:
    - 20.0/6.0mm (#3) 7J - upper ground rail (blue stripe), hole 7 _______
    - 20.0/6.0mm (#3) 12J - upper ground rail (blue stripe), hole 12 _______
    - 20.0/6.0mm (#3) 7F - 7E ______
    - 20.0/6.0mm (#3) 12F - 12E ______
    - 22.5/8.5mm (#4) 7D - 11D ______
    - 22.5/8.5mm (#4) 12D - 16D ______
    - 17.5/3.5mm (#2) 12A - lower ground rail (blue stripe), hole 12 _______
    - 17.5/3.5mm (#2) 21A - lower ground rail (blue stripe), hole 21 _______
- Flip board upside down and hold with vise or 3rd hand tool. Solder all 16 joints _______
- Inspect with magnifying glass to make sure all joints are good and there are no solder bridges _______
- Trim all 16 leads _______
- Test ground plane:
- Test continuity:
- Upper ground rail to lower ground rail _______
- Upper ground rail to all holes in row 7 _______
- Upper ground rail to holes A-E in row 11 _______
- Upper ground rail to all holes in row 12 _______
- Upper ground rail to holes A-E in row 16 _______
- Upper ground rail to holes A-E in row 21 _______
- Test NON-continuity:
- Upper ground rail to upper/lower power rail ______
- Upper ground rail to holes:
  - 6J ______
  - 8J ______
  - 11J ______
  - 13J ______
  - 6E ______
  - 8E ______
  - 10E ______
  - 13E ______
  - 14E ______
  - 15E ______
  - 17E ______
  - 20E ______
  - 22E ______

# Step 9: RED (+5V) wires

- Solder RED (+5V) wires to Perma-Proto (8 joints):
- Only the ones with both ends connecting to Perma-Proto holes
- Insert all wires before soldering. Tape down on front to hold in place. Lengths (total/insulation template#) and holes:
    - 17.5/3.5mm (#2) 8J - upper power rail (red stripe), hole 8 _______
    - 17.5/3.5mm (#2) 13J - upper power rail (red stripe), hole 13 _______
    - 17.5/3.5mm (#2) 19J - upper power rail (red stripe), hole 19 _______
    - 21.5/7.5mm (#A) 17E - 19F _______
- Flip board upside down and hold with vise or 3rd hand tool. Solder all 8 joints _______
- Inspect with magnifying glass to make sure all joints are good and there are no solder bridges _______
- Trim all 8 leads _______
- Test power plane:
- Test continuity:
- Upper power rail to holes F-J in row 8 _______
- Upper power rail to holes F-J in row 13 _______
- Upper power rail to holes F-J in row 19 _______
- Upper power rail to holes A-E in row 17 _______
- Test NON-continuity:
- Upper power rail to upper/lower ground rail _______
- Upper power rail to holes:
  - 9J _______
  - 14J _______
  - 18J _______
  - 20J _______
  - 18D _______

# Step 10: BLUE (and one GREEN) wires

- Solder BLUE (and ONE GREEN) wires to Perma-Proto (6 joints):
- Only the BLUE ones with both ends connecting to Perma-Proto holes
- Only the very short GREEN one
- Insert all wires before soldering. Tape down on front to hold in place. Lengths (total/insulation template#) and holes:
    - 27.5/13.5mm (#6) 11H - 17H (BLUE) _______
    - 15.0/1.0mm (#1) 20J - 21J (BLUE insulation optional) _______
    - 15.0/1.0mm (#1) 9I - 10I (GREEN insulation optional) _______
- Flip board upside down and hold with vise or 3rd hand tool. Solder all 6 joints. _______
- Inspect with magnifying glass to make sure all joints are good and there are no solder bridges _______
- Trim all 6 leads _______
- Test BLUE (and ONE GREEN) wire soldering:
- Test continuity:
- Hole 9F to hole 10F _______
- Hole 11F to hole 17F _______
- Hole 20F to hole 21F _______
- Test NON-continuity:
- Hole 8F to hole 9F _______
- Hole 10F to hole 11F _______
- Hole 11F to hole 12G _______
- Hole 16F to hole 17F _______
- Hole 17F to hole 18F _______
- Hole 19G to hole 20G _______
- Hole 21F to hole 22F _______

# Step 11: 1/4W resistors

- Solder 1/4W resistors to Perma-Proto (16 solder joints):
- Insert all resistors before soldering. Tape down on front to hold in place.
- R1 (150k): 20F - 20D _______
- R2 (7.5k): 21F - 21D _______
- R3 (1k): 6B - 10B _______
- R4 (1k): 17G - 21G _______
- R5 (22k): 13A - 17A _______
- R6 (22k): 19H - 22H _______
- Rf (75k): 15C - 19C _______
- Rg (1k): 16B - 19B _______
- Flip board upside down and hold with vise or 3rd hand tool. Solder all 16 joints _______
- Inspect with magnifying glass to make sure all joints are good and there are no solder bridges _______
- Trim all 16 leads _______
- Use multimeter to measure exact resistances of soldered resistors:  Measuring between the specified Perma-Proto holes listed below also verifies the soldering.
- R1 (150k): 20I - 20A ____________
- R2 (7.5k): 21I - 21B ____________
- R3 (1k): 6E – 10A ____________
- R4 (1k): 17J - 21I ____________
- R5 (22k): 13E - 17D ____________
- R6 (22k): 19I - 22G ____________
- Rf (75k): 15E – 19D ____________
- Rg (1k): 16E – 19D ____________

The measured values of R1, R2, Rf, and Rg could be useful, so keep this record. All values should be within the tolerance of the resistors if the soldering was done correctly.

- Additional tests of resistor soldering:
- Test NON-continuity:
- Hole 6A to hole 7C _______
- Hole 9A to hole 10A _______
- Hole 10A to hole 11A _______
- Hole 12B to hole 13B _______
- Hole 13B to hole 14B _______
- Hole 14E to hole 15E _______
- Hole 15E to hole 16E _______
- Hole 16E to hole 17D _______
- Hole 19A to hole 20A _______
- Hole 20B to hole 21B _______
- Hole 16J to hole 17J _______
- Hole 19I to hole 20I _______
- Hole 21I to hole 22I _______

# Step 12: IC sockets

- Solder IC sockets to Perma-Proto (16 joints):
- Insert both sockets before soldering. Tape down on front to hold in place.
- Make sure notch is on the left end
- TLV2462 (left) socket:
- Pin 1: hole 8E ________
- Pin 5: hole 11F _______
- MCP3202 (right) socket:
- Pin 1: hole 13E ________
- Pin 5: hole 16F ________
- Flip board upside down and hold with vise or 3rd hand tool and solder all 16 joints ________
- Inspect with magnifying glass to make sure all joints are good

________

- Test socket soldering:
- Test continuity:
    - TLV2462 (left) socket hole 1 (lower left) to Perma-Proto hole 8C ______
    - TLV2462 (left) socket hole 2 to Perma-Proto hole 9C ______
    - TLV2462 (left) socket hole 3 to Perma-Proto hole 10C ______
    - TLV2462 (left) socket hole 4 to Perma-Proto ground rails ______
- TLV2462 (left) socket hole 5 (upper right) to Perma-Proto hole 11J ______
- TLV2462 (left) socket hole 6 to socket hole 7 ______
    - TLV2462 (left) socket hole 7 to Perma-Proto hole 9G ______
    - TLV2462 (left) socket hole 8 to Perma-Proto upper power rail ______
- MCP3202 (right) socket hole 1 (lower left) to Perma-Proto hole 13B ______
    - MCP3202 (right) socket hole 2 to Perma-Proto hole 14B ______
    - MCP3202 (right) socket hole 3 to Perma-Proto hole 15B ______
    - MCP3202 (right) socket hole 4 to Perma-Proto ground rails ______
- MCP3202 (right) socket hole 5 (upper right) to Perma-Proto hole 16G ______
    - MCP3202 (right) socket hole 6 to Perma-Proto hole 15J ______
    - MCP3202 (right) socket hole 7 to Perma-Proto hole 14J ______
    - MCP3202 (right) socket hole 8 to Perma-Proto upper power rail ______
- Test NON-continuity:
- TLV2462 socket hole 1 to Perma-Proto ground rails ______
- TLV2462 socket hole 1 to socket hole 2 ______
- TLV2462 socket hole 2 to socket hole 3 ______
- TLV2462 socket hole 3 to socket hole 4 ______
- TLV2462 socket hole 5 to Perma-Proto ground rails ______
- TLV2462 socket hole 5 to socket hole 6 ______
- TLV2462 socket hole 7 to socket hole 8 ______
- TLV2462 socket hole 8 to Perma-Proto ground rails ______
- MCP3202 socket hole 1 to Perma-Proto ground rails ______
- MCP3202 socket hole 1 to socket hole 2 ______
- MCP3202 socket hole 2 to socket hole 3 ______
- MCP3202 socket hole 3 to socket hole 4 ______
- MCP3202 socket hole 4 to Perma-Proto hole 17D ______
- MCP3202 socket hole 5 to Perma-Proto hole 17J ______
- MCP3202 socket hole 5 to socket hole 6 ______
- MCP3202 socket hole 6 to socket hole 7 ______
- MCP3202 socket hole 7 to socket hole 8 ______
- MCP3202 socket hole 8 to Perma-Proto ground rails ______

# Step 13: Filter capacitors

- Solder 0.1uF capacitors to Perma-Proto (4 joints):
- Insert both capacitors before soldering. Bend leads on back to hold in place.
      - C3: 7G - 8G ________
      - C6: 12G - 13G ________
- Flip board upside down and hold with vise or 3rd hand tool and solder both joints ________
- Inspect with magnifying glass to make sure joints are good and there are no solder bridges ________
- Trim all 4 leads _______
- Solder 2.2nF capacitors to Perma-Proto (4 joints):
- Insert both capacitors before soldering. Bend leads on back to hold in place.
      - C4: 10C - 11C ________
      - C5: 11I – 12I ________
- Flip board upside down and hold with vise or 3rd hand tool and solder both joints ________
- Inspect with magnifying glass to make sure joints are good and there are no solder bridges ________
- Trim all 4 leads _______
- Test capacitor soldering
- Test continuity:
- C3 left leg (7G) to Perma-Proto ground rails _______
    - C3 right leg (8G) to Perma-Proto upper power rail _______
    - C6 left leg (12G) to Perma-Proto ground rail _______
- C6 right leg (13G) to Perma-Proto upper power rails _______
- C4 left leg (10C) to Perma-Proto TLV2462 socket hole 3 _______
- C4 right leg (11C) to Perma-Proto ground rails _______
- C5 left leg (11I) to Perma-Proto TLV2462 socket hole 5 _______
- C5 right leg (12I) to Perma-Proto ground rails _______
- Test NON-continuity:
- C3 left leg (7G) to Perma-Proto hole 6G _______
- C3 left leg (7G) to C3 right leg (8G) _______
- C3 right leg (8G) to Perma-Proto hole 9G _______
- C6 left leg (12G) to Perma-Proto hole 11G _______
- C6 left leg (12G) to C6 right leg (13G) _______
- C6 right leg (13G) to Perma-Proto hole 14G _______
- C4 left leg (10C) to Perma-Proto hole 9C _______
- C4 left leg (10C) to C4 right leg (11C) _______
- C5 left leg (11I) to Perma-Proto hole 10I _______
- C5 left leg (11I) to C5 right leg (12I) _______
- C5 right leg (12I) to Perma-Proto hole 13I _______

# Step 14: Two more GREEN wires, one WHITE wire

- Solder one more GREEN wire to Perma-Proto (2 joints):
- Insert wire and tape down on front to hold in place. Length (total/insulation template#) and holes:
    - 40.5/26.5mm (#B) 9G - 14C _______

Bend and route between the IC sockets in a Z (on top of black wires)

- Flip board upside down and hold with vise or 3rd hand tool and solder both joints ________
- Inspect with magnifying glass to make sure joints are good and there are no solder bridges ________
- Trim both leads ________
- Solder one more GREEN wire to Perma-Proto (2 joints):
- Insert wire and tape down on front to hold in place. Length (total/insulation template#) and holes:
    - 40.5/26.5mm (#B) 9C - 19D ______

Route around capacitor C4 and over the top of the previous green wire

- Flip board upside down and hold with vise or 3rd hand tool and solder both joints ________
- Inspect with magnifying glass to make sure joints are good and there are no solder bridges ________
- Trim both leads _______
- Solder one WHITE wire to Perma-Proto (2 joints):
- Insert wire and tape down on front to hold in place. Length(total/insulation template#) and holes:
- 36.0/22.0mm (#C) 8A - 15B _______

This wire should NOT lie flat, but should be a small "arch" to leave clearance for the blue wire to connect to hole 13B

- Flip board upside down and hold with vise or 3rd hand tool and solder both joints ________
- Inspect with magnifying glass to make sure joints are good and there are no solder bridges ________
- Trim both leads _______
- Test GREEN and WHITE wire soldering:
- Test continuity:
- TLV2462 socket hole 1 to MCP3202 socket hole 3 ________
- TLV2462 socket hole 2 to Perma-Proto hole 19A ________
- TLV2462 socket hole 7 to MCP3202 socket hole 2 ________
- Test NON-continuity:
- TLV2462 socket hole 1 to Perma-Proto ground rails ________
- TLV2462 socket hole 1 to socket hole 2 ________
- TLV2462 socket hole 2 to socket hole 3 ________
- TLV2462 socket hole 7 to socket hole 8 ________
- MCP3202 socket hole 1 to socket hole 2 ________
- MCP3202 socket hole 2 to socket hole 3 ________
- Perma-Proto hole 18A to hole 19A ________
- Perma-Proto hole 19A to hole 20A ________

# Step 15: Insert bleed resistor

- Insert 47ohm bleed resistor Rb:
- Tape down on front to hold in place, but don't solder yet
- 6H - 6C _______

# Step 16: Insert load capacitors

- Insert 1000uF load capacitors:
- Tape down on front to hold in place, but don't solder yet
    - 1J - 4J (shorter lead / stripe side (-) on the right (4J), IMPORTANT!) ________
    - 1A - 4A (shorter lead / stripe side (-) on the right (4A), IMPORTANT!) ________

# Step 17: Solder bleed resistor

- Solder 47ohm bleed resistor Rb leads (2 joints):
- DO NOT TRIM LEADS
- Note that the resistor may have to be raised slightly to fit
- Leads are thick so they take a longer time to heat up enough to melt solder
- Solder to holes 6H and 6C with leads straight through holes (i.e. not bent) ________

# Step 18: Shunt resistor

- Solder .005 ohm shunt resistor to *BACK* of Perma-Proto (2 joints):
- Bend leads at right angle so resistor is CENTERED between bends and the lead ends are 27.5mm apart ________
- Insert shunt resistor leads into the following holes FROM THE BACK of the Perma-Proto:
- 4E - lower ground rail (blue stripe), hole 13 ________
- Tape down on back to hold in place ______
- Flip board face-up and hold with vise or 3rd hand tool and solder both joints (long heavy leads will take time to heat) ________
- Inspect with magnifying glass to make sure joints are good and there are no solder bridges ________
- Trim both leads _______

# Step 19: Prepare load circuit zip cord

- Prepare load circuit zip cord:
- NOTE: This can be any stranded AWG 18 or AWG 16 insulated wire such as from a typical household extension/lamp cord or heavier speaker wire. AWG 18 solid core is fine too.
- "A": PV- binding post to lower ground rail and shunt
- Cut to length: 9cm ________
- Strip 1cm on each end and twist strands ________
- Crimp cable ring connector on one end using pliers (or vise / ViseGrips / crimping tool) ________
- Heat crimp with the soldering iron and flow solder into strands ________
- Heat the strands of the other twisted end and flow solder into the strands (i.e. "tin" it) ________
- "B": PV+ binding post to relay module NO terminal
- Cut to length: 9cm ________
- Strip 1cm on each end and twist strands ________
- Crimp cable ring connector on one end using pliers (or vise / ViseGrips / crimping tool) ________
- Heat crimp with the soldering iron and flow solder into strands ________
- Heat the strands of the other twisted end and flow solder into the strands (i.e. "tin" it) ________
- "C": Load capacitors (+) side to relay module C terminal
- Cut to length: 11cm ________
- Strip 1cm on each end and twist strands ________
- Heat the strands of both ends and flow solder into the strands (i.e. "tin" them) ________

# Step 20: Load capacitor (+) leads

- Solder (+) load capacitor leads to each other and to zip cord "C"(1 large joint):
- DON'T COVER UP MOUNTING HOLE!
- Leave enough room for standoff, but don't put standoff in hole when soldering; it will suck heat and wires won't get hot enough to flow solder
- Bend lead from hole 1A so it lies flat and in the correct direction and contacts lead from hole 1J. See photo. ________
- Solder leads to their holes (1J and 1A) ________
- Solder capacitor leads to each other ________
- Tack on zip cord “C” so it extends toward the top of the board, parallel to the end. Heat up tinned end of wire and capacitor leads enough to completely reflow the solder (add more solder if needed). See photo. ________
- Make sure there is no solder bridging to any of the row 4 holes (rows 1, 2, and 3 are ok) ________

# Step 21: Load capacitor (-) leads

- Solder (-) load capacitor leads to each other, shunt resistor, and lead of 47ohm bleed resistor Rb that comes through hole 6C (1 large joint):
- Use needle-nosed pliers to wrap Rb lead around shunt resistor lead between its body and hole (may also need to cut off some of Rb lead) ________
- Bend capacitor (-) leads to contact shunt resistor lead at E4. See photo. ________
- Solder leads to their holes (4J and 4A) ________
- Solder capacitor (-) leads to each other and to shunt resistor lead at E4, and also make sure solder flows to Rb lead that is wrapped around shunt resistor lead ________
- Trim other Rb lead ________

# Step 22: Zip cord “A”

- Solder zip cord “A” to shunt/ground
- Tack zip cord “A” onto the end of the shunt resistor that is connected to the lower ground rail. Orient it so it extends toward the top of the board. Heat up tinned end of wire and shunt lead enough to completely reflow the solder (add more solder if needed). See photo. ________

# Step 23: Test previous 8 steps

- Test bleed resistor, shunt resistor, and load capacitor soldering:
- Measure capacitance between Perma-Proto holes 1F and 4F. It should be between 1600uF and 2400uF (most likely on the smaller end) ________
- Use multimeter to measure resistance between Perma-Proto holes:
    - Rb (47ohms): 6J - 6A _________
    - Shunt: 6A - ground rails _________

NOTE: Shunt is only .005 ohms, which is below the resolution of the multimeter. Measured value should be approximately the same as shorting the probes together.

- Test NON-continuity:
- Capacitor (-) leads to capacitor (+) leads on back ________
- Hole 6J to ground rails ________ (47Ω)

# Step 24: Insert ICs

Static electricity can destroy ICs. Take off your shoes and touch something metal connected to ground before handling them, if possible.

- Insert TLV2462 in left socket _________
- Make sure dot is on the left end (pin 1)
- Legs may have to be bent inward slightly
- Insert MCP3202 in right socket __________
- Make sure notch and dot are on the left end (pin 1)
- Legs may have to be bent inward slightly

# Step 25: Off-Perma-Proto hookup wires

- Solder off-Perma-Proto hookup wires to Perma-Proto:
- Cut all wires to length, with 7mm insulation stripped from each end:
    - BLUE, 8.5cm ________
    - BLUE, 8.5cm ________
    - YELLOW, 7.0cm ________
    - YELLOW, 15.0cm ________
    - GREEN, 7.0cm ________
    - GREEN, 13.0cm ________
    - WHITE, 7.0cm ________
    - RED, 11.0cm ________
    - BLACK, 7.0cm ________
- Use 3rd hand tool to hold wire in hole and perpendicular to the board while soldering
- Solder BLUE wires (2 joints):
- Perma-Proto hole 13B (8.5cm) ________
- Perma-Proto hole 22I (8.5cm) ________
- Solder YELLOW wires (2 joints):
- Perma-Proto hole 14G (7.0cm) ________
- Perma-Proto hole 20C (15.0cm) ________
- Solder GREEN wires (2 joints):
- Perma-Proto hole 6I (13.0cm) ________
- Perma-Proto hole 15G (7.0cm) ________
- Solder WHITE wire (1 joint):
- Perma-Proto hole 16G ________
- Solder RED wire (1 joint):
- Perma-Proto upper power rail (red stripe), hole 15 ________
- Solder BLACK wire (1 joint):
- Perma-Proto lower ground rail (blue stripe), hole 15 ________
- Inspect with magnifying glass to make sure joints are good and there are no solder bridges ________
- Trim all 9 leads ________
- Test off-Perma-Proto hookup wire soldering:
- Test continuity:
- Lower BLUE wire (stripped end) to MCP3202 pin 1 ________
- Upper BLUE wire (stripped end) to Perma-Proto hole 22F ________
- Lower YELLOW wire (stripped end) to Perma-Proto hole 20A ________
- Upper YELLOW wire (stripped end) to MCP3202 pin 7 ________
- Left GREEN wire (stripped end) to Perma-Proto hole 6J ________
- Right GREEN wire (stripped end) to MCP3202 pin 6 ________
- WHITE wire (stripped end) to MCP3202 pin 5 ________
- RED wire (stripped end) to Perma-Proto hole 19I ________
- BLACK wire (stripped end) to Perma-Proto hole 7I ________
- Test NON-continuity:
    - Lower BLUE wire (stripped end) to Perma-Proto hole 7I ________
    - Lower BLUE wire (stripped end) to Perma-Proto hole 9J ________
- Upper BLUE wire (stripped end) to Perma-Proto hole 21I ________
- Lower YELLOW wire (stripped end) to Perma-Proto hole 19A ________
- Lower YELLOW wire (stripped end) to Perma-Proto hole 21B ________
- Upper YELLOW wire (stripped end) to Perma-Proto hole 13I ________
- Upper YELLOW wire (stripped end) to Perma-Proto hole 15I ________
    - Left GREEN wire (stripped end) to Perma-Proto hole 7I ________ (47Ω)
- Right GREEN wire (stripped end) to Perma-Proto hole 14I ________
- Right GREEN wire (stripped end) to Perma-Proto hole 16I ________
    - WHITE wire (stripped end) to Perma-Proto hole 15I ________
    - WHITE wire (stripped end) to Perma-Proto hole 17I ________
- RED wire (stripped end) to Perma-Proto hole 7I ________
    - BLACK wire (stripped end) to Perma-Proto hole 19I ________

# Step 26: Solder Male-Female relay jumpers to Perma-Proto

- Solder Male-Female relay module power/control jumper wires to Perma-Proto:
- This assumes the relay module has jumper pins on the power and control inputs (some have screw terminals, like the load side)
- Solder BLUE jumper (cut pin off) (1 joint):
- This one needs to have its pin cut off and that end stripped. This is because the pin and its plastic housing are too tall to fit next to the Arduino in the case.
- Solder stripped end to Perma-Proto hole 22J ________
- Solder RED jumper pin (1 joint):
- Perma-Proto upper power rail (red stripe), hole 10 ________
- Inspect with magnifying glass to make sure joints are good and there are no solder bridges ________
- Trim lead of BLUE jumper (don’t trim pin from RED jumper) ________
- Test soldering of Male-Female relay module power/control jumper wires to Perma-Proto:
- Test continuity:
- Need to insert a wire into female end for these
- BLUE jumper to Perma-Proto hole 22F ________
- RED jumper to Perma-Proto hole 19I ________
- Test NON-continuity:
- BLUE jumper to Perma-Proto hole 21I ________
- RED jumper to Perma-Proto hole 7I ________

# Step 27: Solder bypass diodes in series (NO LONGER NEEDED)

NOTE: The original design called for two 15A, 45V bypass diodes (15SQ045), but this was a design error. A single 15A, 100V diode must be used.

# Step 28: Make binding post connections

- Make binding post connections:
- Remove outer nuts and washers from threaded post ________
- Insert negative (black side) threaded post through the cable ring connector on zip cord “A” (other end is attached to shunt resistor and ground rail on bottom of Perma-Proto) ________
- Insert positive (red side) threaded post through the cable ring connector on zip cord “B” ________
- Bend 100V diode leads into loops that will fit onto the threaded posts (NOTE: photos show two 45V diodes) ________
- Slide looped ends of the diode leads onto the threaded posts with the STRIPED END OF THE DIODE TOWARD THE RED SIDE ________
- Put washers back on, over the diode lead loops ________
- Put nuts on and tighten (not too tight – they’ll be coming off again later) ________

# Step 29: Make relay switching side connections

- Make relay module switching side (screw-down) connections:
- Twist end of zip cord “B” (from red side of binding posts) to end of yellow wire that comes from Perma-Proto hole 20C, and solder them together ________
- Loosen screw and insert the twisted/soldered end into the top (“Normally Open” - NO) screw terminal hole on the relay module and tighten down the screw. Tug the wires gently to make sure they are securely connected. _________
- Loosen screw and insert the end of zip cord “C” (other end is attached to capacitor + leads on back of Perma-Proto) into the center (“Common” - C) screw terminal hole on the relay module and tighten down the screw. _________
- Loosen screw and insert the end of the green wire that comes from Perma-Proto hole 6I into the bottom (“Normally Closed – NC) screw terminal hole on the relay module and tighten down the screw. __________

# Step 30: Make relay power/control side connections

- Make relay module control/power side (jumper) connections:
- Connect the BLUE jumper (from Perma-Proto hole 22J) to the IN pin on the relay module __________
- Connect the RED jumper (from Perma-Proto upper power rail hole 10) to the VCC pin on the relay module __________
- Connect the BLACK jumper from the GND pin on the relay module to the GND pin on the Arduino (“Power” side) __________

# Step 31: Make other Arduino connections

- Make other Arduino connections:
- Connect the BLUE wire from Perma-Proto hole 22I to Arduino pin 2 __________
- Connect the BLUE wire from Perma-Proto hole 13B to Arduino pin 10 __________
- Connect the WHITE wire from Perma-Proto hole 16G to Arduino pin 11 __________
- Connect the GREEN wire from Perma-Proto hole 15G to Arduino pin 12 __________
- Connect the YELLOW wire from Perma-Proto hole 14G to Arduino pin 13 __________
- Connect the RED wire from Perma-Proto upper power rail (red stripe), hole 15 to Arduino +5V pin

__________

- Connect the BLACK wire from Perma-Proto lower ground rail (blue stripe), hole 15 to Arduino GND (near pin 13) __________

# Step 32: Test system connections

- Test system connections:
- Test continuity:
- RED binding post to Perma-Proto hole 20A ________
- BLACK binding post to Arduino GND pin (on back) ________
- Relay module “NC” terminal (on back) to Perma-Proto hole 6J (or resistor Rb lead) ________
- Relay module IN pin (on back) to Arduino pin 2 (on back) ________
- Relay module GND pin (on back) to Perma-Proto upper ground rail ________
- Relay module VCC pin (on back) to Perma-Proto upper power rail ________
- MCP3202 pin 1 to Arduino pin 10 (on back) ________
- MCP3202 pin 5 to Arduino pin 11 (on back) ________
- MCP3202 pin 6 to Arduino pin 12 (on back) ________
- MCP3202 pin 7 to Arduino pin 13 (on back) ________
- Perma-Proto upper ground rail to Arduino GND pin (on back) ________
- Perma-Proto upper power rail to Arduino 5V pin (on back) ________
- Test NON-continuity:  NOTE: temporarily disconnect the RED wire from the Arduino 5V pin for these tests (OR expect ~1.5kΩ resistance between VCC and GND in last test).
    - RED binding post to BLACK binding post ________
    - Relay module IN pin (on back) to relay module GND pin (on back) ________
    - Relay module IN pin (on back) to relay module VCC pin (on back) ________
    - Relay module GND pin (on back) to relay module VCC pin (on back) ________
- Measure resistance:
- BLACK binding post to Perma-Proto hole 1F ________ (should be 47 ohms)

# Step 33: System bench test

- System bench test:
- Connect Arduino to laptop via USB
- Check for smoke _______
- Check that relay module red LED is on and green LED is off ________
- Check that Arduino yellow LED is blinking once per second (assuming that it’s still loaded with “Blink” sketch) _______
- Load IV Swinger 2 Arduino sketch
- Open Arduino application on your computer ________
- Find where the Arduino software looks for sketches:  Arduino->Preferences->Sketchbook location
- Use your browser to go to:  https://raw.githubusercontent.com/csatt/IV_Swinger/master/Arduino/IV_Swinger2/IV_Swinger2.ino
- Right-click and use “Save As” to save IV_Swinger.ino to the Arduino sketchbook folder found above (make sure your browser doesn’t add an extension like .txt to the file name)
- Go back to the Arduino application and find the IV_swinger2.ino sketch using:  File->Open  The Arduino application will inform you that IV_Swinger2.ino must be in a folder named IV_Swinger2 and it will offer to do that for you. Accept its kind offer.
- Click on arrow button or select “Upload” from “Sketch” menu _________
- Check Arduino LEDs: Yellow “TX” LED should be blinking. This is not the same yellow LED that the Blink sketch controls. _________
- “Nothing connected” test
- Open the IV Swinger 2 application ________
- Verify that “Swing!” button text changes to RED and message below it changes from “Not connected” to “Connected” (briefly, then disappears). The “TX” LED should no longer be on. _________  If not, pull down the “USB Port” menu and select the correct port.
- Click the “Swing!” button. You should hear the relay click twice and see an error dialog saying “ERROR: Voc is zero volts” _________
- 9V battery test
- Strip both ends of two wires and screw one end of each into the side holes of the binding posts. If you happen to have a 9V battery snap-on connector, use that. _________
- Connect the wire from the RED binding post to the positive (smaller/male) terminal of a 9V battery (you can either tape it or hold it with your thumb) _________
- Connect the wire from the BLACK binding post to the negative (larger/female) terminal of the same 9V battery (tape it or hold it with the same thumb as the other) _________
- Click the “Swing!” button. You should get an IV curve that looks like the photo.

# Step 34: Prepare for case and final assembly

The acrylic baseball display case used for the IV Swinger 2 enclosure needs to have several holes drilled through it for attachments, and the “fins” on the bottom need to be trimmed off in order for everything to fit.

Case side definitions:

- Front: side with the USB connector
- Back: side opposite from front
- Left: side with binding posts and Perma-Proto
- Right: side with relay module
- Bottom: side with Arduino
- Top: side closest to capacitors

The case comes in two U-shaped halves:

- Base: Left / Bottom (with fins) / Right
- Lid: Front / Top / Back

All the attachments are made to the base half. The lid half has nothing attached to it, but does need a 3/8” hole in the front for the USB cable.

Care must be taken when drilling acrylic or else it will crack:

- Use a drill press if you have one
- Use vise (with rubber guards) to hold case
- Position so that the hole being drilled is close to the vise jaw
- Start with 1/16” pilot for all holes
- Drill slowly with light pressure
- Spray water on hole as it is being drilled to cool
- Use a Forstner bit to drill the 3/8” hole for the USB cable. Otherwise, you’ll have to start with 1/16” pilot and drill incrementally larger holes until you get to 3/8”

# Step 35: Cut off fins

- Cut fins:  There are three fins on the bottom of the case (to cradle the baseball). Their tips need to be cut off so the Arduino clears them when it is on its standoffs. (Using longer standoffs is another possibility.)  A coping saw or hacksaw can be used for this, among other possibilities. Just be careful not to crack or scratch the case.  Cut off as much as possible, but at least enough so standoffs are longer than the remaining height.  _________

# Step 36: Mark holes for Arduino standoffs

IMPORTANT: For this step and the next three, look straight down when making the Sharpie dots (the plastic distorts/refracts if you look at an angle, and you’ll miss the mark).

- Mark holes for Arduino standoffs:
- Attach 4 standoffs to Arduino:
- Disconnect all wires from Arduino _______
- Insert threaded/male end of each standoff through its hole in the Arduino from the back ________
- Screw nuts onto the threaded ends of the standoffs on the front of the Arduino – hold the nut with your finger and turn the standoff to tighten it. Use pliers to tighten more.  NOTE: The hole nearest the Arduino reset button doesn’t have room for a nut ________
- Place the Arduino in position, standing on its standoffs (including the one without a nut). The Arduino should be touching the right side of the case, with the USB connector facing the front. The single fin should be facing toward you so the fins look like a “Y”. See photo. ________
- PUT LID ON THE CASE. This is important because the fit is very tight! ________
- Turn the case over and look at it from the bottom. The Arduino will probably stay in place, but you can make sure by squeezing the front and back together with the hand you’re holding it with. Use a Sharpie to mark the centers of the four holes. ________
- Remove the lid from the case and remove the Arduino ________

# Step 37: Mark holes for Perma-Proto standoffs

- Mark holes for Perma-Proto:
- Attach 2 standoffs to Perma-Proto:
- Insert threaded/male end of each standoff through its hole in the Perma-Proto from the back. Don’t worry if the one on the capacitor end touches the soldered capacitor leads. ________
- Screw nuts on the threaded ends of the standoffs on the front of the Perma-Proto and tighten them ________
- Place the Perma-Proto in position. Leave 2-3mm on the side near the front. Align so the capacitors are 2-3mm below the top (if they are angled up at all, make sure the ends will be low enough not to contact the lid). _________
- Use Sharpie to mark the centers of the two holes _________

# Step 38: Mark holes for relay module standoffs

- Mark holes for relay module:
- Attach 4 standoffs to relay module:
- Disconnect any remaining wires from relay module ________
- Insert threaded/male end of each standoff through its hole in the relay module from the back ________
- Screw nut on the threaded end on the front of the relay module and tighten it ________
- Use the Sharpie to make a dot on the right side of the case at the following position:
- 1.0 cm from the left (i.e. front) edge
- 1.5 cm from the top edge  ________
- Hold the relay in position inside the case, with the hole of the upper left standoff aligned with the Sharpie dot. You can hold it with one hand and mark with the other – or use a small clamp to hold it in place. _________
- Use Sharpie to mark the centers of the other three holes _________

# Step 39: Mark holes for binding posts

- Mark holes for binding posts:
- Remove top nuts, washers, diodes, cable rings, and bottom nuts from the binding posts. Remove the black plastic backing plate. ________
- Hold the plastic backing plate in position on the inside of the left side of the case. It should be about 1mm from the rear inner edge of the case and about 1mm from the bottom. ________
- Use Sharpie to mark the centers of the two holes ________

# Step 40: Drill 12 marked holes

- Drill 12 marked holes:
- Use something pointy to make an indentation in the middle of each of the 12 Sharpie marks. The tip of the Forstner bit is perfect for this, but you can also use a needle or the tip of an X-acto blade (poke and twirl). This will keep the drill bit centered when you start drilling the hole. ________
- Drill twelve 1/16” pilot holes ________
- Switch to 9/64” bit and re-drill all 12 holes ________
- Enlarge 2 holes for binding posts:
- Switch to 11/64” bit and re-drill both of the binding post holes ________
- Switch to 13/64” bit and re-drill both of the binding post holes one more time ________
- Clean up case:
- Remove burrs around holes with X-acto knife or your fingernails ________
- Wash case off and dry ________

# Step 41: Install binding posts

- Install binding posts:
- Insert the binding posts through their holes with the RED terminal toward the TOP of the case ________
- Slide backing plate over the posts on the inside of the case ________
- Thread nuts on the posts and tighten down ________

# Step 42: Install Perma-Proto

- Install Perma-Proto in case:
- Insert the Perma-Proto into the case and screw down its two standoffs with two M3 screws ________

# Step 43: Make binding post connections

- Make connections to binding posts:
- Slide cable ring connector on zip cord “A” (from Perma-Proto) onto negative (BLACK side) threaded post ________
- Slide cable ring connector on zip cord “B” (other end soldered to yellow wire from Perma-Proto) onto positive (RED side) threaded post ________
- Put washers back on, over the cable ring connectors ________
- Slide looped ends of the diode leads onto the threaded posts with the STRIPED END OF THE DIODES TOWARD THE RED SIDE ________
- Put nuts on and tighten down securely ________

# Step 44: Install Arduino

- Install Arduino in case:
- Attach the one Arduino standoff that won’t have a nut onto the bottom of the case with an M3 screw ________
- Insert the Arduino, put the lid on the case, and screw down the other three standoffs with M3 screws. TIP: start all screws before tightening any of them. ________
- Remove the lid ________

# Step 45: Connect Perma-Proto to Arduino

- Connect the 7 wires from the Perma-Proto to the Arduino:  You may need to use needle nosed pliers for this unless you have small hands
- Connect the BLUE wire from Perma-Proto hole 22I to Arduino pin 2 __________
- Connect the BLUE wire from Perma-Proto hole 13B to Arduino pin 10 __________
- Connect the WHITE wire from Perma-Proto hole 16G to Arduino pin 11 __________
- Connect the GREEN wire from Perma-Proto hole 15G to Arduino pin 12

__________

- Connect the YELLOW wire from Perma-Proto hole 14G to Arduino pin 13 __________
- Connect the BLACK wire from Perma-Proto ground rail, hole 15 to Arduino GND ________
- Connect the RED wire from Perma-Proto power rail, hole 15 to Arduino +5V pin

________

# Step 46: Connect screw-down side of relay module

- Connect wires to screw-down side of relay module:

This needs to be done BEFORE the relay module is attached to the case, while you still have screwdriver access.

- Insert the twisted/soldered end of zip cord “B” (from RED binding post) and yellow wire (from Perma-Proto) into the top (“Normally Open” - NO) screw terminal hole on the relay module and tighten down the screw. Tug the wires gently to make sure they are securely connected. _________
- Insert the end of zip cord “C” (from back of Perma-Proto) into the center (“Common” - C) screw terminal hole on the relay module and tighten down the screw. Tug gently to test. _________
- Insert the end of the green wire that comes from Perma-Proto hole 6I into the bottom (“Normally Closed – NC) screw terminal hole on the relay module and tighten down the screw. Tug gently to test. __________

# Step 47: Install relay module

- Install relay module in case:
- Insert the relay module into the case and screw down its standoffs with four M3 screws. TIP: start all screws before tightening any of them. ________

# Step 48: Connect relay module jumpers

- Connect wires to jumper side of relay module:
- Connect the BLUE jumper (from Perma-Proto hole 22J) to the IN pin on the relay module _________
- Connect the BLACK jumper from the GND pin on the relay module to the GND pin on the Arduino _________
- Connect the RED jumper (from Perma-Proto upper power rail hole 10) to the VCC pin on the relay module _________

# Step 49: Drill USB connector hole

- Drill USB connector hole:
- Put the lid on the case _________
- Make indentation in the exact center of the USB connector using the tip of the Forstner bit (or whatever pointy thing you used for the other drill-starting indentations). NOTE: it is very important that this hole is precisely centered. You need to look at it from all four directions before making the indentation since the refraction through the plastic distorts the apparent position (you’ll see what I mean as soon as you turn it 90 degrees). _________
- Use 3/8” Forstner bit to drill the hole
- Drill slowly, spraying with water often
- Reduce pressure when hole is getting close to “punching through”
- Alternative to Forstner bit is to use following succession of normal bits:
  - 1/16”, 1/8”, 3/16”, 1/4”, 5/16”, 3/8” (untested – may need even smaller (1/32”) steps)

_________

- Clean up the edge of the hole with X-acto knife or your fingernail __________
- Wash lid off and dry ________
- Put lid on and insert the USB cable to make sure it fits ________
- If it doesn’t, try loosening the Arduino standoff screws. This might give you enough “play” to get the connector in. Then, with the connector still in, re-tighten the screws
- If that isn’t enough, you may have to enlarge the hole with a round file or some other way

# Step 50: Make PV cables

- Make PV cables:

To connect to a standard PV module, you need cables with MC4 connectors.

It is not necessary to use the same heavy gauge cable that is used in a rooftop solar installation (and on the modules themselves), assuming you only need them to be a few feet long. The nice thing about the binding posts is that you can easily swap cables with longer or shorter ones depending on the situation. The main reason for longer cables would be so the laptop and IV Swinger 2 can be in a shady spot away from the panel. These instructions intentionally do not specify the length or type of the PV cables because it is so dependent on the usage.

If you decide that shorter cables are OK, you can just use the same zip cord that you used for the internal load connections. The only tricky part is that crimping the MC4 connectors onto smaller wire gauge doesn't really work - you need to solder them on. You also should use solder to tin the bare ends that insert into the binding posts so they are more durable.

The downside to the binding posts is that it is possible to connect the wrong cable to the wrong post. The bypass diodes between the binding posts protect against this, but it's still a good idea to make it as foolproof as possible. Put some red tape around the one that connects to the red binding post and some black tape around the one that connects to the black binding post.

The cable with the female MC4 connector connects to the RED binding post.

The cable with the male MC4 connector connects to the BLACK binding post.

# Step 51: Final test

Your IV Swinger 2 is now complete!

Repeat the tests you did for the “system bench test” to make sure everything got hooked back up correctly.

You may now test it with a real PV module.

If some amount of accuracy is important to you, see the IV Swinger 2 User Guide for instructions on how to perform a calibration. There is also a Help dialog available from the Calibrate menu in the application.

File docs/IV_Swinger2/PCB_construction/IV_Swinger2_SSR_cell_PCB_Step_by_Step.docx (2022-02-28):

# IV Swinger 2


Step-by-step Construction:

Arduino Shield PCB Designs
**SSR cell version**

Document Revision: 1.03 (27-Feb, 2022) Chris Satterlee

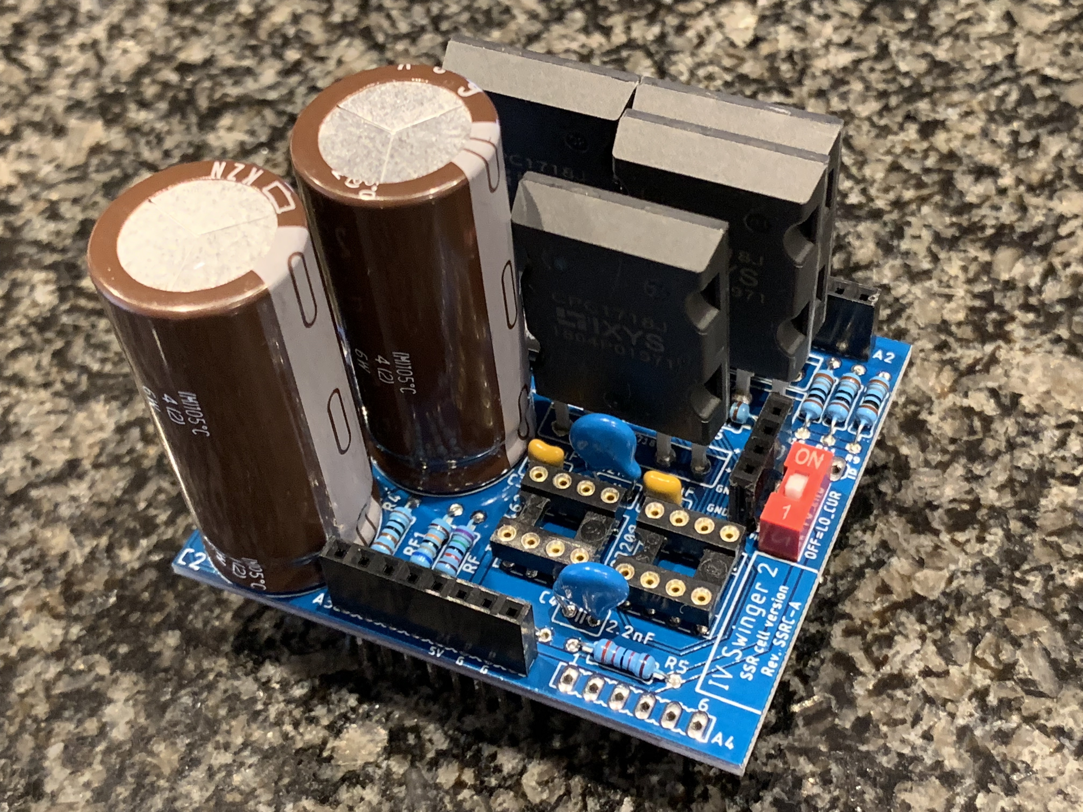
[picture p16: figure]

Copyright (C) 2022 Chris Satterlee

IV Swinger and IV Swinger 2 are open source hardware and software projects.

Permission to use the hardware design is granted under the terms of the TAPR Open Hardware License Version 1.0 (May 25, 2007) - http://www.tapr.org/OHL

Permission to use the software is granted under the terms of the GNU General Public License v3 - http://www.gnu.org/licenses.

Current versions of the license files, documentation, PCB files, and software can be found at:

https://github.com/csatt/IV_Swinger

Intro

This document contains the step-by-step instructions to build the EMR cell variant of IV Swinger 2.

These are the same instructions that are on www.instructables.com but do not include any of the photos or videos. The purpose of this document is primarily so you can print it out and check off completed steps and make other notes as you work on the project. You should use the Instructable to take advantage of the visual aids.

https://www.instructables.com/id/IV-Swinger-2-a-50-IV-Curve-Tracer

# Step 1: Understand the HW design / Choose Variant

Please refer to the Instructable for this Step.

https://www.instructables.com/id/IV-Swinger-2-a-50-IV-Curve-Tracer

The remainder of this document assumes that you have chosen the following variant:

PV cell version,

solid-state relay (SSR)

https://github.com/csatt/IV_Swinger/raw/master/PCB/IV_Swinger_2_ss_cell/PDF/IV_Swinger_2_ss_cell_sch.pdf

If this is not correct, please find the step-by-step construction document for the version you did choose. Many of the steps are similar, but the details differ, so you need to use the correct document.

# Step 2: Install software

Before spending time building the hardware, install the Arduino software and the IV Swinger 2 application on the laptop that you’ll be using.

- Install Arduino IDE:

https://www.arduino.cc/en/Main/Software

- Install IV Swinger 2 app:

https://github.com/csatt/IV_Swinger/releases

- Make sure both of the above come up before proceeding. If necessary, upgrade the OS on your computer

# Step 3: Order PCB

Currently the PCB must be purchased from a manufacturing house that will actually fabricate it for your order. The downside of this is that you’ll probably have to buy more than you need. I have used the following two:

OSH Park:

https://oshpark.com

Made in USA

Cost: $25 for 3 PCBs (includes shipping)

Time: < 12 days to ship

PCBWay:

https://www.pcbway.com

Made in China

Cost: $5 for 10 PCBs + shipping ($16 DHL to CA)

Time: < 5 days to ship

Amazingly, I have put orders in to PCBWay on a Monday and had the boards in my hands in California on Friday.

I have shared this PCB design on PCBWay, and you can order it directly using the following link:

https://www.pcbway.com/project/shareproject/W112835ASR5_IV_Swinger_2_ss_cell_Rev_A_2019_01_06_546bb8c1.html

https://www.pcbway.com/project/shareproject/W112835ASR5_IV_Swinger_2_ss_cell_Rev_A_2019_01_06_546bb8c1.html

Alternately, you can order PCBs from OSH Park (or anywhere else) by uploading the ZIP archive of the Gerber files, which are found in the GitHub repository:

IV_Swinger/PCB/IV_Swinger_2_ss_cell/Gerber/*.zip

Soon, I hope to find someone who wants to sell individual PCBs on eBay (possibly in kits, that include all the other parts too).

# Step 4: Buy other parts

The other necessary parts to build an IV Swinger 2 can all be purchased online from Amazon and Digi-Key.

SSR PV cell version BOM:

https://github.com/csatt/IV_Swinger/raw/master/PCB/BOM/ssr_cell_BOM.pdf

The BOM has an Amazon link and a Digi-Key link at the bottom. The Amazon link is a “wish list” that can be used to populate your cart. Some of the items come in quantities larger (in some cases much larger) than needed to build a single IV Swinger 2. You may of course choose to find equivalents that are offered in smaller quantities. Also, many of the items are things that you may already have, so don’t necessarily just blindly order everything on the list.

The Digi-Key link is a pre-populated shopping cart. Again, you’ll want to check if you already have any of the items before ordering.

In both cases, it is possible (or probable) that certain items will go out of stock or be discontinued, so you’ll have to find suitable substitutions. Note that there are some of the Digi-Key items have ALT_n (e.g., ALT_1, ALT_2) in the “Customer Reference field. These should only be ordered if the primary version of the same part is marked as “backorder”.

Alternately, the following CSV file may be used to order from Digi-Key, Mouser or possibly other suppliers that support uploading a BOM spreadsheet. It includes the manufacturer, manufacturer’s part number, Digi-Key part number, and Mouser part number:

https://github.com/csatt/IV_Swinger/raw/master/PCB/BOM/DigiKeyMouser/ssr_cell_DigiKey_Mouser.csv

https://github.com/csatt/IV_Swinger/raw/master/PCB/BOM/DigiKeyMouser/ssr_cell_DigiKey_Mouser.csv

Also included below is the link to donate to the original Arduino developers. I donate $5 for each $10 Arduino clone that I buy. This is your choice, but I think it is the right thing to do.

Donate to Arduino.cc:
https://www.arduino.cc/en/Main/Contribute

# Step 5: Gather / buy tools

- Holding:
  - Vise
  - 3rd hand tool with magnifying glass
  - Tape (preferably Kapton, but Scotch ok)
  - Long/needle-nosed pliers
- Soldering:
  - Soldering iron (preferably temp controlled solder station)
  - Tip cleaner
  - Rosin core solder
  - Solder sucker or solder wick
- Cutting:
  - Wire cutter (flush cut)
  - Wire stripper
- Drilling:
  - Drill
  - 1/16" bit (pilot for 9/64")
  - 9/64" bit (standoffs)
  - 11/64" bit (pilot for 13/64")
  - 13/64" bit (binding posts)
  - 3/8" Forstner bit (preferred - USB cable hole)
    - Alternate: 1/8”, 3/16”, 7/32”, 1/4”, 9/32”, 5/16”, 11/32”, 3/8”, and 25/64” normal bits
- Other:
  - Digital Multimeter (DMM)
  - Small Phillips screwdriver
  - 1.5V battery
  - Sharpie
  - Ruler
  - Water spray bottle

# Step 6: Prepare for Soldering

- Soldering NOTES:
- If you don't have a lot of soldering experience, read this:

https://learn.adafruit.com/adafruit-guide-excellent-soldering/common-problems

- Soldering components to the PCB is pretty mistake-proof, but doing it in the order described is recommended (shortest -> tallest).
- Some components have a correct and an incorrect orientation and some don’t matter. Pay attention to the instructions.
- I highly recommend using 63/37 0.031” (or 0.8mm) rosin core solder. Yes, it is 37% lead, but it is not a health risk for you (really), and environmentally insignificant when used by hobbyists. You’ll solder like a pro.

# Step 7: 1/4W resistors

Resistors can be inserted in either orientation. It is very important to use the correct value for each, however.

- Solder 1/4W resistors to PCB:
- Insert all resistors before soldering. Tape down on front to hold in place OR bend leads slightly on back.

PV cell version (SSR) – 20 joints:

- R3 (1k): _______
- R4 (1k): _______
- R5 (22k): _______
- R6 (180Ω): _______ (180 ohms not k!)
- R9 (180Ω): _______
- R10 (180Ω): _______
- R11 (180Ω): _______
- RF (75k): _______
- RF1 (680k): _______
- RG (1k): _______
- Flip board upside down and hold with vise or 3rd hand tool OR tape board to work surface. Solder all 20 leads _______
- Inspect with magnifying glass to make sure all joints are good and there are no solder bridges _______  NOTE: A solder bridge is ok between the ends of RF and RG
- Trim all leads _______
- Use multimeter to measure exact resistances of soldered resistors:  With the PCB still upside down, measure the resistances with a DMM. The resistances (but unfortunately not the names) are marked on the back. Record the exact values of the ones marked with an asterisk (*) below – these values will be used later (“Step 27: Apply resistor calibration”). The others should just be close to their specified value (should be 1%, but don’t worry as long as it is < 10%) - the main point is to catch any mistakes you might have made.

PV cell version (SSR):

- R3 (1k): _______
- R4 (1k): _______
- R5 (22k): _______
- R6 (180Ω): _______ (180 ohms not k!)
- R9 (180Ω): _______
- R10 (180Ω): _______
- R11 (180Ω): _______
- RF (75k): _______ *
- RF1 (680k): _______ *
- RG (1k): _______ *

# Step 8: IC sockets

- Solder IC sockets to PCB – 16 joints:
- Insert both sockets before soldering. Tape down on front to hold in place.
- Make sure notch is on the left end as marked on the PCB
- Flip board upside down and hold with vise or 3rd hand tool OR tape board to work surface and solder all 16 pins ________
- Inspect with magnifying glass to make sure all joints are good

________

If you have opted not to use sockets, solder the ICs directly to the PCB instead of the sockets. Make sure dot is on the left end of the TLV2462 (pin 1). Make sure notch and dot are on the left end of the MCP3202 (pin 1).

# Step 9: Horizontal shunt resistor

The shunt resistor lies flat on the PCB and should be soldered down at this point.

- Solder horizontal shunt resistor to PCB – 2 joints:
- Insert 5mΩ shunt resistor (either way). Tape down to hold in place.
      - SHUNT: ________
- Flip board upside down and hold with vise or 3rd hand tool OR tape board to work surface and solder both leads ________
- Trim both leads _______
- Re-flow/add solder on both leads _______

(This is because leads are thick, and may not have heated well before trimming)

- Inspect with magnifying glass to make sure joints are good

________

# Step 10: Stacking connectors and female header

- Solder stacking connectors and female header to PCB – 30 joints:
- Insert stacking connectors A1, A2, and A3 and female header FH. These connectors are symmetrical, so there’s no “backwards”. Tape down to hold in place.
      - A1 (10 pin): ________
      - A2 (8 pin): ________
      - A3 (8 pin): ________
      - FH (4 pin): ________

NOTE: Stacking connector A4 is not needed.

- Flip board upside down and hold with vise or 3rd hand tool OR tape board to work surface and solder all pins ________

NOTE: the pins on A1, A2, and A3 that are actually used on the PCB are circled on the back of the PCB. Soldering the others provides physical support only.

- Inspect with magnifying glass to make sure joints are good and there are no solder bridges ________

# Step 11: DIP switch or jumper header

The cell versions need either a x1 DIP switch or a 2-pin jumper header. Both have the same purpose – to select whether current measurements are multiplied by a factor of approximately 10 (for lower power PV cells). Only one of these should be installed.

- Solder x1 DIP switch (or jumper header) to PCB – 2 joints:
- Insert x1 DIP switch with the “ON” end toward the top of the board. Tape down to hold in place.
      - OFF=LO_CUR: ________

-OR-

- Insert 2-pin jumper header. Tape down to hold in place.
      - JP: ________
- Flip board upside down and hold with vise or 3rd hand tool OR tape board to work surface and solder both pins ________
- Inspect with magnifying glass to make sure joints are good and there are no solder bridges ________

# Step 12: Screw terminal blocks

- Solder screw terminal blocks to PCB – 4 joints:
- Insert screw terminal blocks with the openings facing left. Tape down to hold in place.
      - J1: ________
      - J2: ________

NOTE: The screw terminal blocks may be omitted entirely, soldering the 18ga wire directly to the holes in the PCB (later).

- Flip board upside down and hold with vise or 3rd hand tool OR tape board to work surface and solder all joints ________
- Inspect with magnifying glass to make sure joints are good and there are no solder bridges ________

# Step 13: Filter capacitors

The small filter capacitors are not polarized, so it doesn’t matter which lead goes in which hole.

- Solder 0.1uF capacitors to PCB - 4 joints:
- Insert both capacitors before soldering. Bend leads on back to hold in place.
      - C3: ________
      - C6: ________
- Flip board upside down and hold with vise or 3rd hand tool and solder all four joints ________
- Inspect with magnifying glass to make sure joints are good and there are no solder bridges ________
- Trim all 4 leads _______
- Solder 2.2nF (2200pF) capacitors to PCB - 4 joints:
- Insert both capacitors before soldering. Bend leads on back to hold in place.
      - C4: ________
      - C5: ________
- Flip board upside down and hold with vise or 3rd hand tool and solder all four joints ________
- Inspect with magnifying glass to make sure joints are good and there are no solder bridges ________
- Trim all 4 leads _______

# Step 14: Bypass diode

The purpose of the bypass diode is to protect the electronics in case the PV is connected to the IV Swinger 2 backwards.

The cell versions require one 15A, 45V bypass diode (15SQ045).

- Solder bypass diode(s) to PCB – 2 or 4 joints:
- Bend lead on striped end of diode around the diode so that it points in the same direction as the other lead.
- Insert leads as follows:
      - Pad D1, striped end (top): ________
      - Pad D2, non-striped end (bottom): ________
- Flip board upside down and hold with vise or 3rd hand tool and solder both (or all four) leads ________
- Trim leads _______
- Re-flow/add solder on both/all leads _______

(This is because leads are thick, and may not have heated well before trimming)

- Inspect with magnifying glass to make sure joints are good

________

# Step 15: Solid-state relays

- Solder SSRs to PCB – 16 joints:
- Put two SSRs (SSR1 and SSR5) side-by-side in vise with leads pointing straight up. Try to make sure they are aligned so they will look nice. ________
- Lower the PCB over the leads. It is very important that the front of the SSRs is pointed toward the middle of the PCB. The front is the black side with the label. The back has the metal heat sink pad. Hold the PCB with the 3rd hand tool so the leads all extend the same amount as the stacking connector pins and are perpendicular to the PCB.  The bodies of the SSRs should not be sitting flat on the PCB; there should be some separation (~1cm) for heat dissipation.

________

- Solder all 8 SSR1/SSR5 leads ________
- Trim all 8 SSR1/SSR5 leads ________
- Insert SSR6 in its position with its back against the front of SSR5 and tape it to SSR5.

________

- Flip board upside down and hold with vise or 3rd hand tool ________
- Solder all 4 SSR6 leads ________
- Trim all 4 SSR6 leads ________
- Insert SSR4 in the vise, pins up, with the SSR perpendicular to the vise jaws.
- Lower the PCB over the leads. It is very important that the front of the SSR is pointed toward the middle of the PCB. Hold the PCB with the 3rd hand tool so that the pins of SSR4 extend the same as the leads of the other SSRs and are perpendicular to the PCB.

________

- Solder all 4 SSR4 leads ________
- Trim all 4 SSR4 leads _______
- Re-flow/add solder on all 16 leads _______
- Inspect with magnifying glass to make sure joints are good

________

# Step 16: Load capacitors

- Solder load capacitors to PCB:

Cell versions use 22000µF, 6.3V load capacitors.

These are polarized electrolytic capacitors, so orientation is important.

- Insert load capacitors in position. Stripe side (shorter lead) goes to the right – this is the negative lead. Tape to hold in place.
    - C1 ________
    - C2 ________
- Flip board upside down and hold with vise or 3rd hand tool ________
- Solder all 4 leads ________
- Trim all 4 leads _______
- Re-flow/add solder on all 4 leads _______

(This is because leads are thick, and may not have heated well before trimming)

- Inspect with magnifying glass to make sure joints are good

________

# Step 17: Optionally clean flux residue from PCB

Some people think it is important to clean off the flux residue from the PCB after soldering. It makes it looks nicer, but since the PCB sits on top of the Arduino, you don’t see the back anyway.

Functionally, it shouldn’t matter. The solder manufacturer Kester says this:

“Rosin flux residues are non-conductive and non-corrosive. Under normal circumstances they do not have to be removed from a printed circuit assembly. Rosin residue removal would be for cosmetic considerations. In an environment where the working temperature of the assembly will exceed 200°F the rosin residues will melt and become conductive, in these situations flux removal is required.”

If you do want to clean it off, see this Instructable: https://www.instructables.com/id/Cleaning-up-your-PCB/

# Step 18: Check for shorts

Using the digital multimeter (DMM) set on the continuity check (beep), check that there is no continuity between the following:

Power to ground (mandatory):

- Left IC socket, pin 8 to pin 4 OR
- Right IC socket, pin 8 to pin 4

Other (recommended):

- All “neighbor” pins or solder joints. None should indicate continuity, except the pairs circled in the pictures.
- The idea is to find solder bridges that you didn’t see visually

# Step 19: Insert ICs

Static electricity can destroy ICs. Take off your shoes and touch something metal connected to ground before handling them, if possible.

- Insert TLV2462 in left socket _________
- Make sure dot is on the left end (pin 1)
- Legs may have to be bent inward slightly
- Insert MCP3202 in right socket __________
- Make sure notch and dot are on the left end (pin 1)
- Legs may have to be bent inward slightly

# Step 20: Prepare load circuit wires

- Prepare load circuit wires:
- NOTE: This can be any stranded AWG 18 or AWG 16 insulated wire such as from a typical household extension/lamp cord or heavier speaker wire. AWG 18 solid core is fine too. If solid core is used, ignore the instructions to twist and “tin” the strands. And instead of the ring connectors, the end can just be bent into a loop (add 1 cm to length).
- "BLK1": BLK1 (lower black) binding post to B1 screw terminal on PCB (J1) “RED1”: RED1 (lower red) binding post to R1 screw terminal on PCB (J1) “BLK2”: BLK2 (upper black) binding post to B2 screw terminal on PCB (J2) “RED2”: RED2 (upper red) binding post to R2 screw terminal on PCB (J2)
- Cut to length: BLK1 (7cm): ________

RED1 (7cm): ________
BLK2 (9cm): ________
RED2 (9cm): ________

- Strip 1 cm on each end and twist strands BLK1 ________

RED1 ________
BLK2 ________
RED2 ________

- Crimp cable ring connector on one end using pliers (or vise / ViseGrips / crimping tool) BLK1 ________ RED1 ________ BLK2 ________ RED2 ________
- Heat crimp with the soldering iron and flow solder into strands BLK1 ________ RED1 ________ BLK2 ________ RED2 ________
- Heat the strands of the other twisted end and flow solder into the strands (i.e. "tin" it) BLK1 ________ RED1 ________ BLK2 ________ RED2 ________

# Step 21: Make load circuit connections

Refer to the drawings of off-PCB connections for this step. These connections use the load circuit wires that were prepared in the previous step.

- Make binding post connections:
- Remove outer nuts and washers from threaded posts ________
- Insert threaded post of black side through the cable ring connector on load circuit wire: “BLK1” ________
- Insert threaded post of red side through the cable ring connector on load circuit wire: “RED1”

________

- Insert threaded post of black side of second binding post through the cable ring connector on load circuit wire: “BLK2” ________
- Insert threaded post of red side of second binding post through the cable ring connector on load circuit wire: “RED2“ ________
- Put washers back on ________
- Put nuts on and tighten ________
- Make PCB connections:
- Loosen screw and insert the twisted/soldered end of the load circuit wire from the black binding post into the lower hole of screw terminal J1 and tighten down the screw. “BLK1” _________
- Loosen screw and insert the twisted/soldered end of the load circuit wire from the red binding post into the adjacent hole of screw terminal J1 and tighten down the screw. “RED1”

_________

- Loosen screw and insert the twisted/soldered end of the load circuit wire from the second black binding post into the lower hole of screw terminal J2 and tighten down the screw. “BLK2 _________
- Loosen screw and insert the twisted/soldered end of the load circuit wire from the second red binding post into the upper hole of screw terminal J2 and tighten down the screw. “RED2” _________

# Step 22: Check all off-PCB connections

- Check all off-PCB connections:
- Use the drawing of off-PCB connections for the version you are building and double-check that all connections match the drawing.  __________
- Tug all wires connected to screw-terminal blocks gently to make sure they are securely connected.  __________

# Step 23: Mate PCB with Arduino

- Mate PCB with Arduino:
- Put tape on metal USB connector housing where PCB will touch it ________
- Line up stacking connector pins on bottom of the PCB with the corresponding connectors on the top of the Arduino and press the boards together, taking care not to bend any of the pins. ________
- For now, move the slider on the DIP switch that was installed in “Step 11: DIP switch or jumper header” above to the ON position. If you opted to install jumper header JP instead, slide the jumper over the pins to short them together.  __________

# Step 24: Smoke test

- Smoke test:
- Connect Arduino to laptop via USB
- Check for smoke _______  Check that Arduino yellow LED is blinking once per second (assuming that it’s still loaded with “Blink” sketch) _______

# Step 25: Load Arduino sketch

- Load IV Swinger 2 Arduino sketch:
- Open Arduino application on your computer ________
- Find where the Arduino software looks for sketches:  Arduino->Preferences->Sketchbook location
- Use your browser to go to:  https://raw.githubusercontent.com/csatt/IV_Swinger/master/Arduino/IV_Swinger2/IV_Swinger2.ino
- Right-click and use “Save As” to save IV_Swinger.ino to the Arduino sketchbook folder found above (make sure your browser doesn’t add an extension like .txt to the file name)
- Go back to the Arduino application and find the IV_swinger2.ino sketch using:  File->Open  The Arduino application will inform you that IV_Swinger2.ino must be in a folder named IV_Swinger2 and it will offer to do that for you. Accept its kind offer.
- Click on arrow button or select “Upload” from “Sketch” menu _________
- Check Arduino LEDs: Yellow LED should be blinking. This is not the same yellow LED that the Blink sketch controls. _________

# Step 26: Connect via IV Swinger 2 app

- Connect via IV Swinger 2 application:
- Open the IV Swinger 2 application ________
- Verify that “Swing!” button text changes to RED and the message below it changes from “Not connected” to “Connected” (briefly, then disappears). The yellow LED should no longer be on. _________  If not, pull down the “USB Port” menu and select the correct port. If it isn’t obvious which one to select:
- Close the IV Swinger 2 application and disconnect the IV Swinger 2 USB cable from the laptop
- Re-open the IV Swinger 2 application (leave the cable disconnected)
- Pull down the USB Port menu and take note of the listed ports
- Connect the USB cable from the IV Swinger 2 hardware to the laptop
- Pull down the USB Port menu and select the port that is new to the list

# Step 27: Apply resistor calibration

- Apply resistor calibration:
- In the IV Swinger 2 app, select “Resistors” from the “Calibrate” menu ________
- Enter the values you measured and recorded in “Step 7: 1/4W resistors” above.
- Values are in ohms
- IMPORTANT: You must enter a value of 0.0 for R1 (which does not exist on cell versions). Do not change the value for R2.
- Note that there is no RF1 value to enter. This is by design. Later (not now!), you will enter the value of RF+RF1 for RF if you set the DIP switch to the OFF position (or remove the jumper).

________

# Step 28: Sanity tests

- Sanity tests:
- “Nothing connected” test
- Click the “Swing!” button. You should see an error dialog saying “ERROR: Voc is zero volts” _________
- Battery test

Use 1.5V battery

- Strip both ends of two wires and screw one end of each into the side holes of the binding posts. If you happen to have a battery connector or holder with wires, use that. Use the RED1 and BLK1 binding posts. Leave RED2 and BLK2 unconnected. _________
- Connect the wire from the RED1 binding post to the positive terminal of the battery (you can either tape it or hold it with your thumb/finger) _________
- Connect the wire from the BLK1 binding post to the negative terminal of the same battery _________
- Click the “Swing!” button. You should get an IV curve that looks like the photo. _________
- If you get an error dialog that says: “ERROR: Voc is zero volts” check that you don’t have the battery backwards and that the wires are making good contact with the terminals.
- If you get an error dialog that says: “ERROR: Timed out polling for stable Isc”
- Click on Preferences, click on Arduino tab, change value of “Isc stable ADC” to 500, click OK
- Retry the battery test; it should work
- Click on Preferences, click on Arduino tab, click on “Restore Defaults”, click OK

# Step 29: Prepare for case and final assembly

The acrylic baseball display case used for the IV Swinger 2 enclosure needs to have several holes drilled through it for attachments.

Case side definitions (see photo):

- Front: side with the USB connector
- Back: side opposite from front
- Left: side with binding posts
- Right: side opposite from left
- Bottom: side with Arduino
- Top: side above PCB

The case comes in two U-shaped halves:

- Base: Left / Bottom (with fins) / Right
- Lid: Front / Top / Back

All the attachments are made to the base half. The lid half has nothing attached to it, but does need a 3/8” hole in the front for the USB cable.

Care must be taken when drilling acrylic or else it will crack:

- Use a drill press if you have one
- Use vise (with rubber guards) to hold case
- Position so that the hole being drilled is close to the vise jaw
- Start with 1/16” pilot for all holes
- Drill slowly with light pressure
- Spray water on hole as it is being drilled to cool
- Use a Forstner bit to drill the 3/8” hole for the USB cable. Otherwise, you’ll have to start with 1/16” pilot and drill incrementally larger holes until you get to 3/8” (actually 25/64”)

# Step 30: Mark holes for Arduino standoffs

IMPORTANT: For this step and the next three, look straight down with one eye when making the Sharpie dots (the plastic distorts/refracts if you look at an angle, and you’ll miss the mark).

- Mark holes for Arduino standoffs:
- Attach four 15mm standoffs to Arduino:
- Unplug the USB cable from the Arduino _______
- Carefully remove the PCB from the Arduino _______
- Insert threaded/male end of each standoff through its hole in the Arduino from the back ________
- Screw nuts onto the threaded ends of the standoffs on the front of the Arduino – hold the nut with your finger and turn the standoff to tighten it. Use pliers to tighten more.  NOTE: The hole nearest the Arduino reset button doesn’t have room for a nut ________
- Place the Arduino in position, standing on its standoffs (including the one without a nut). The Arduino should be touching the right side of the case, with the USB connector facing the front. The single fin should be facing toward you so the fins look like a “Y”. See photo. ________
- PUT LID ON THE CASE. This is important because the fit is very tight! ________
- Turn the case over and look at it from the bottom. The Arduino will probably stay in place, but you can make sure by squeezing the front and back together with the hand you’re holding it with. Use a Sharpie to mark the centers of the four holes. ________
- Remove the lid from the case and remove the Arduino ________

# Step 31: Mark holes for binding posts

- Mark holes for binding posts:
- Remove top nuts, washers, cable rings, and bottom nuts from the binding posts. Remove the black plastic backing plate. ________
- Hold the plastic backing plate in position on the inside of the left side of the case. It should be about 1mm from the front inner edge of the case and about 1mm from the bottom. ________
- Use Sharpie to mark the centers of the two holes ________
- Repeat the above for the upper pair of binding posts, which goes immediately above the first pair, with the top of the backing plate 1mm from the top ________

# Step 32: Drill marked holes

- Drill 8 marked holes:
- Use something pointy to make an indentation in the middle of each of the Sharpie marks. The tip of the Forstner bit is perfect for this, but you can also use a needle or the tip of an X-acto blade (poke and twirl). This will keep the drill bit centered when you start drilling the hole. ________
- Drill 1/16” pilot holes ________
- Switch to 9/64” bit and re-drill all holes ________
- Enlarge holes for binding posts:
- Switch to 11/64” bit and re-drill the binding post holes ________
- Switch to 13/64” bit and re-drill the binding post holes one more time ________
- Clean up case:
- Remove burrs around holes with X-acto knife or your fingernails ________
- Wash case off and dry ________

# Step 33: Install binding posts

- Install binding posts:
- Insert the binding posts through their holes with the RED terminals toward the TOP of the case ________
- Slide backing plates over the posts on the inside of the case ________
- Thread nuts on the posts and tighten down ________

# Step 34: Install Arduino and PCB

- Install Arduino (without PCB) in case:
- Attach the one Arduino standoff that won’t have a nut onto the bottom of the case with an M3 screw ________
- Insert the Arduino, put the lid on the case, and screw down the other three standoffs with M3 screws. TIP: start all screws before tightening any of them. ________
- Remove the lid ________
- Mate PCB back onto Arduino:
- Load circuit wires should still be screwed to PCB. If not, insert them back to into their correct screw terminal block openings and tighten them down. ________
- Line up stacking connector pins on bottom of the PCB with the corresponding connectors on the top of the Arduino and press the boards together, taking care not to bend any of the pins. ________

# Step 35: Restore binding post connections

- Restore connections to binding posts:
- Restore connections as before, following the off-PCB connections drawing. Tighten nuts securely. _________

# Step 36: Drill USB connector hole

- Drill USB connector hole:
- Put the lid on the case _________
- Make indentation in the exact center of the USB connector using the tip of the Forstner bit (or whatever pointy thing you used for the other drill-starting indentations). NOTE: it is very important that this hole is precisely centered. You need to look at it from all four directions before making the indentation since the refraction through the plastic distorts the apparent position (you’ll see what I mean as soon as you turn it 90 degrees). _________
- Use 3/8” Forstner bit to drill the hole
- Drill slowly, spraying with water often
- Reduce pressure when hole is getting close to “punching through”
- Alternative to Forstner bit is to use following succession of normal bits:
  - 1/16”, 1/8”, 3/16”, 7/32”, 1/4”, 9/32”, 5/16”, 11/32”, 3/8”, 25/64”

_________

- Clean up the edge of the hole with X-acto knife or your fingernail __________
- Wash lid off and dry ________
- Put lid on and insert the USB cable to make sure it fits ________
- If it doesn’t, try loosening the Arduino standoff screws. This might give you enough “play” to get the connector in. Then, with the connector still in, re-tighten the screws
- If that isn’t enough, you may have to enlarge the hole with a round file or some other way

# Step 37: Final test

Your IV Swinger 2 is now complete!

Repeat the tests you did in “Step 28: Sanity tests” to make sure everything got hooked back up correctly.

You may now test it with a real PV cell. Refer to the IV Swinger 2 User Guide for information on how to build and connect a bias battery, which is necessary for typical high power PV cells.

If accuracy is important to you, see the IV Swinger 2 User Guide for instructions on how to perform a calibration. There is also a Help dialog available from the Calibrate menu in the application.

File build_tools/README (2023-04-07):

The build_tools directory contains scripts used for building Mac and
Windows executables and packaging them in installers.

Do NOT use this directory for running these tools. If you do that, then
the output files might accidently get committed to the repo, and that is
not what we want.

--------------------------------------------------------------------------------
Instructions for Mac build:

  1) Install pyinstaller:

       % pip install pyinstaller

  2) Install dmgbuild:

       % pip install dmgbuild

  3) Set environment variable $GITHUB to point to the parent directory
     of your clone of the IV_Swinger GitHub repo, e.g.:

       % export GITHUB="$HOME/GitHub"

     Or to make it permanent (assuming you use bash):

       % echo 'export GITHUB="$HOME/GitHub"' >> ~/.bash_profile

  4) Update the version string in $GITHUB/IV_Swinger/python3/version.txt

  5) Complete all testing using straight Python (this assumes that
     you have installed all of the required Python packages):

       % cd $GITHUB/IV_Swinger/python3
       % python IV_Swinger2_gui.py

  6) Create a build folder/directory somewhere NOT under $GITHUB, e.g.:

       % mkdir $HOME/IV_Swinger2_build

  7) Run pyinstaller script in the build folder:

       % cd $HOME/IV_Swinger2_build
       % $GITHUB/IV_Swinger/build_tools/mac_run_pyi

       NOTE: this generates some warnings and errors. See the section
             "Acceptable Mac errors and warnings" below.

  8) Test the generated executable:

       % cd $HOME/IV_Swinger2_build/dist
       % open IV\ Swinger\ 2.app

  9) Apply generic code signature:
 
       % codesign --force --deep -s - IV\ Swinger\ 2.app

 10) Build the DMG with dmgbuild:

       % cd $HOME/IV_Swinger2_build
       % $GITHUB/IV_Swinger/build_tools/mac_build_dmg

 11) Test the DMG:

       % open *.dmg

       Follow instructions to install

 12) Test the installed app by launching from Applications folder

--------------------------------------------------------------------------------
Acceptable Mac errors and warnings

The mac_run_pyi script may generate the following, which are all OK:

 - Anything labeled "INFO:" is ok

 - WARNING: Hidden import "pkg_resources.py2_warn" not found!
 - WARNING: Hidden import "pkg_resources.markers" not found!
 - WARNING: Library Advapi32 required via ctypes not found
 - WARNING: Library setupapi required via ctypes not found
 - WARNING: Library Cfgmgr32 required via ctypes not found
 - WARNING: Library user32 required via ctypes not found
 - WARNING: Ignoring /System/Library/Frameworks/CoreFoundation.framework/CoreFoundation imported from (...) - only basenames are supported with ctypes imports!
 - WARNING: Ignoring /System/Library/Frameworks/IOKit.framework/IOKit imported from (...) - only basenames are supported with ctypes imports!
 - .../site-packages/setuptools/distutils_patch.py:25: UserWarning: Distutils was imported before Setuptools. This usage is discouraged and may exhibit undesirable behaviors or errors. Please use Setuptools' objects directly or at least import Setuptools first.

--------------------------------------------------------------------------------
Instructions for Windows build (Python 3):

NOTE: it is assumed that you already have python and pip installed as
      well as all of the python packages required to run IV_Swinger2_gui.py
      using straight Python (See README file in python3 directory).

  1) Install WiX, pyinstaller, BeautifulSoup4, and lxml:

       http://wixtoolset.org/releases/ (install latest)
         -> add %WIX%bin to your %path%
       pip install pyinstaller
       pip install beautifulsoup4
       pip install lxml

  2) Set environment variable %GITHUB% to point to the parent directory
     of your clone of the IV_Swinger GitHub repo, e.g.:

       set GITHUB=%HOME%\Documents\GitHub
       setx GITHUB %HOME%\Documents\GitHub

  3) Update the version string in %GITHUB%\IV_Swinger\python\version.txt

  4) Complete all testing using straight Python:

       cd %GITHUB%\IV_Swinger\python3
       python IV_Swinger2_gui.py

  5) Create a build folder/directory somewhere NOT under %GITHUB%, e.g.:

       mkdir %HOME%\IV_Swinger2_build

  6) Run the run_pyi.bat script in that folder:

       cd %HOME%\IV_Swinger2_build
       %GITHUB%\IV_Swinger\build_tools\run_pyi.bat

       NOTE: this generates some warnings and errors. See the section
             "Acceptable Windows errors and warnings" below.

  7) Test the generated executable:

       cd %HOME%\IV_Swinger2_build\dist\"IV Swinger 2"
       "IV Swinger 2.exe"

  8) Run the WiX "heat" utility like this:

       cd %HOME%\IV_Swinger2_build
       heat dir ".\dist\IV Swinger 2" -ag -sfrag -sreg -template product -out heat.wxs

       Now you have a file %HOME%\IV_Swinger2_build\heat.wxs

  9) Run the fix_heat_wxs.py script:

       python %GITHUB%\IV_Swinger\build_tools\fix_heat_wxs.py heat.wxs

 10) Run candle (WiX tool):

       candle IV_Swinger2_*.wxs

 11) Run light (WiX tool):

       light -b ".\dist\IV Swinger 2" -sice:ICE60 IV_Swinger2_*.wixobj

 12) Test the installer:

       msiexec /i IV_Swinger2_*.msi /l*v IV_Swinger2.log
     OR
       Find it with Windows Explorer and double-click it

 13) Test the installed app by launching from the Start Menu

--------------------------------------------------------------------------------
Acceptable Windows errors and warnings:

The run_pyi.bat script may generate the following, which are all OK:

 - Anything labeled "INFO:" is ok
 
 - ModuleNotFoundError: No module named 'win32com'
 - ModuleNotFoundError: No module named 'tornado'

 - WARNING: Hidden import "pkg_resources.py2_warn" not found!
 - WARNING: Hidden import "pkg_resources.markers" not found!

 - RuntimeError: The WebAgg backend requires Tornado.

--------------------------------------------------------------------------------

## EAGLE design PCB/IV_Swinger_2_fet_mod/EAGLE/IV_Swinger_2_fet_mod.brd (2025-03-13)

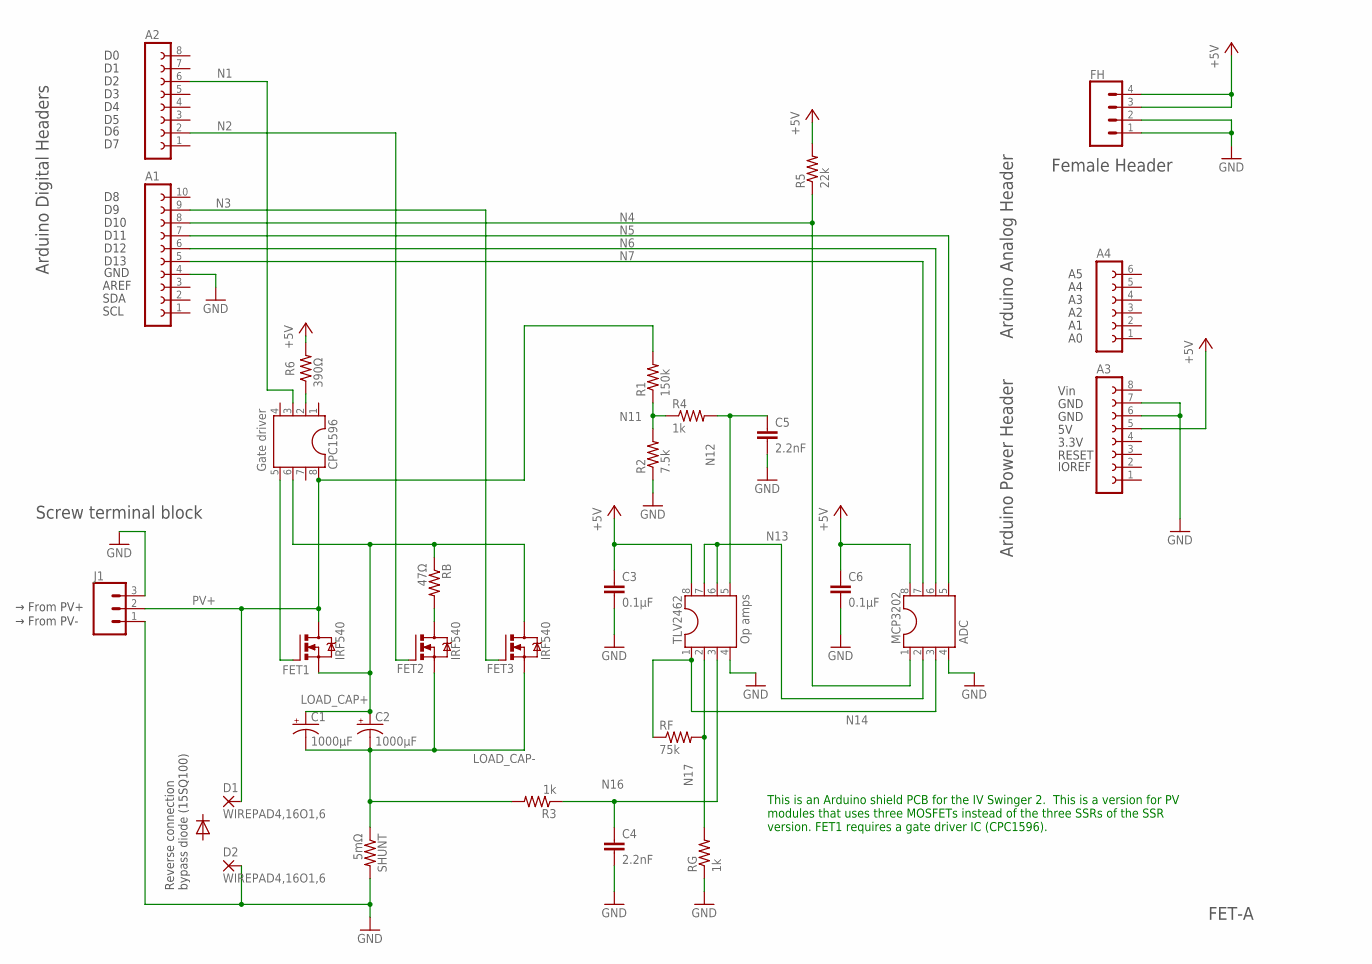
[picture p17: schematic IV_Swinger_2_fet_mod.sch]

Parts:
A1: FE10-1; FE10
A2, A3: FE08-1; FE08
A4: FE06-1; FE06
C1, C2: 1000µF; E7,5-18
C3, C6: 0.1µF; C025-030X050
C4, C5: 2.2nF; C025-030X050
CPC1596: Gate driver; SOCKET-08
D1, D2: WIREPAD4,16O1,6; 4,16O1,6
FET1, FET2, FET3: IRF540; TO220BV
FH: CONN_04LONGPADS; 1X04_LONGPADS
J1: SCREWTERMINAL-5MM-3
MCP3202: ADC; SOCKET-08
R1: 150k; 0207/10
R2: 7.5k; 0207/10
R3, R4: 1k; 0207/10
R5: 22k; 0207/10
R6: 390Ω; 0207/10
RB: 47Ω; P0817V
RF: 75k; 0207/10
RG: 1k; 0207/10
SHUNT: 5mΩ; 0617V
TLV2462: Op amps; SOCKET-08

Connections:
+5V: A3.5, C3.1, C6.1, FH.3, FH.4, MCP3202.8, R5.2, R6.2, TLV2462.8
GND: A1.4, A3.6, A3.7, C3.2, C4.2, C5.2, C6.2, D2.1, FH.1, FH.2, J1.1, J1.3, MCP3202.4, R2.1, RG.1, SHUNT.2, TLV2462.4
LOAD_CAP+: C1.+, C2.+, CPC1596.6, FET1.S, FET3.D, RB.1
LOAD_CAP-: C1.-, C2.-, FET2.S, FET3.S, R3.2, SHUNT.1
N1: A2.6, CPC1596.3
N2: A2.2, FET2.G
N3: A1.9, FET3.G
N4: A1.8, MCP3202.1, R5.1
N5: A1.7, MCP3202.5
N6: A1.6, MCP3202.6
N7: A1.5, MCP3202.7
N11: R1.1, R2.2, R4.1
N12: C5.1, R4.2, TLV2462.5
N13: MCP3202.2, TLV2462.6, TLV2462.7
N14: MCP3202.3, RF.1, TLV2462.1
N16: C4.1, R3.1, TLV2462.3
N17: RF.2, RG.2, TLV2462.2
unnamed: FET2.D, RB.2
unnamed: CPC1596.5, FET1.G
unnamed: CPC1596.2, R6.1
PV+: CPC1596.8, D1.1, FET1.D, J1.2, R1.2

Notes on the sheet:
→ From PV-
Screw terminal block
SCL
SDA
AREF
D13
D12
GND
D10
D11
RESET
3.3V
IOREF
Vin
Arduino Digital Headers
Arduino Analog Header
Arduino Power Header
Female Header
FET-A
This is an Arduino shield PCB for the IV Swinger 2. This is a version for PV modules that uses three MOSFETs instead of the three SSRs of the SSR version. FET1 requires a gate driver IC (CPC1596).
→ From PV+
Reverse connection bypass diode (15SQ100)

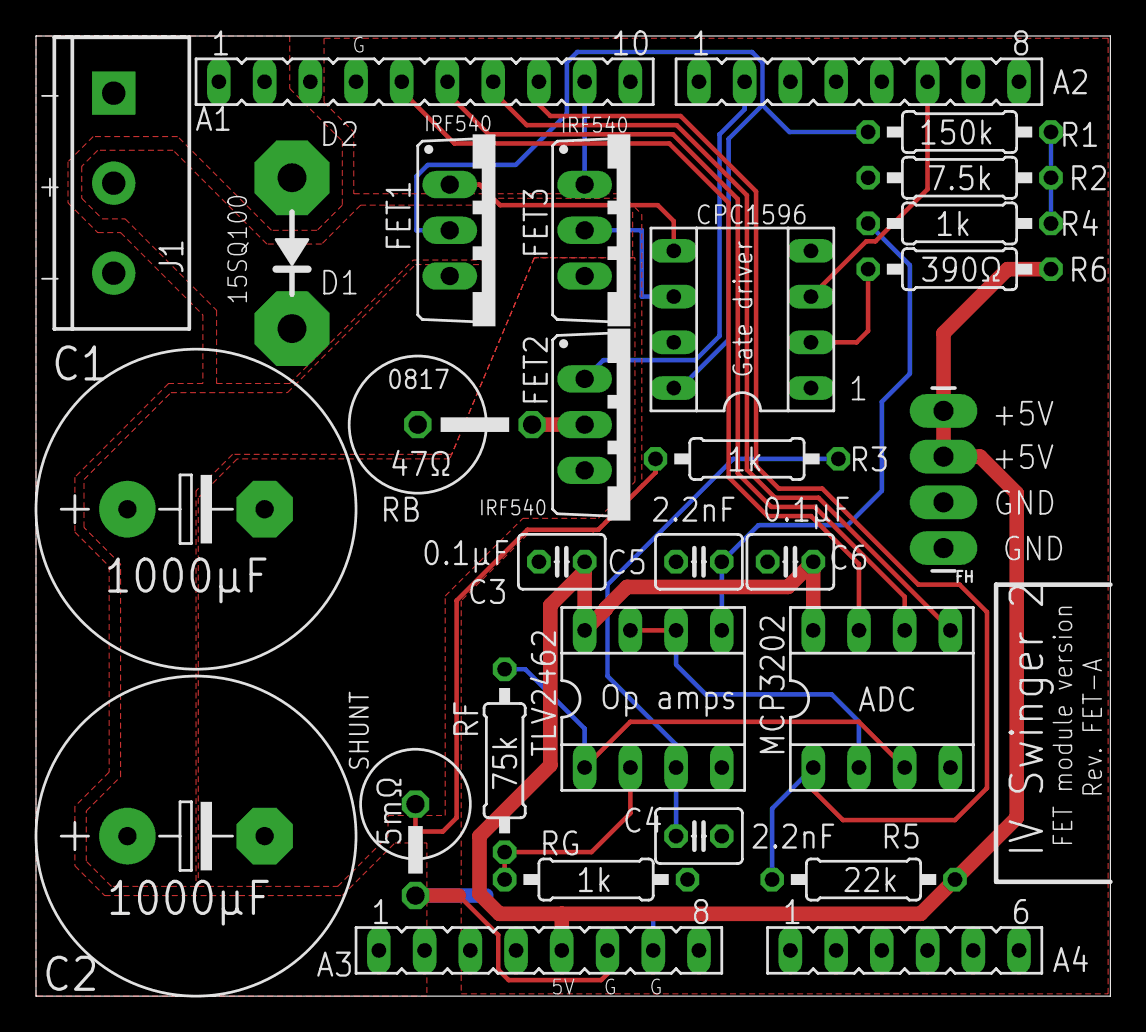
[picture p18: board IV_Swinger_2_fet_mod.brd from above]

Board: 2 copper layers, 59.7 x 53.3 mm, 30 parts (0 on the bottom side), 21 nets.

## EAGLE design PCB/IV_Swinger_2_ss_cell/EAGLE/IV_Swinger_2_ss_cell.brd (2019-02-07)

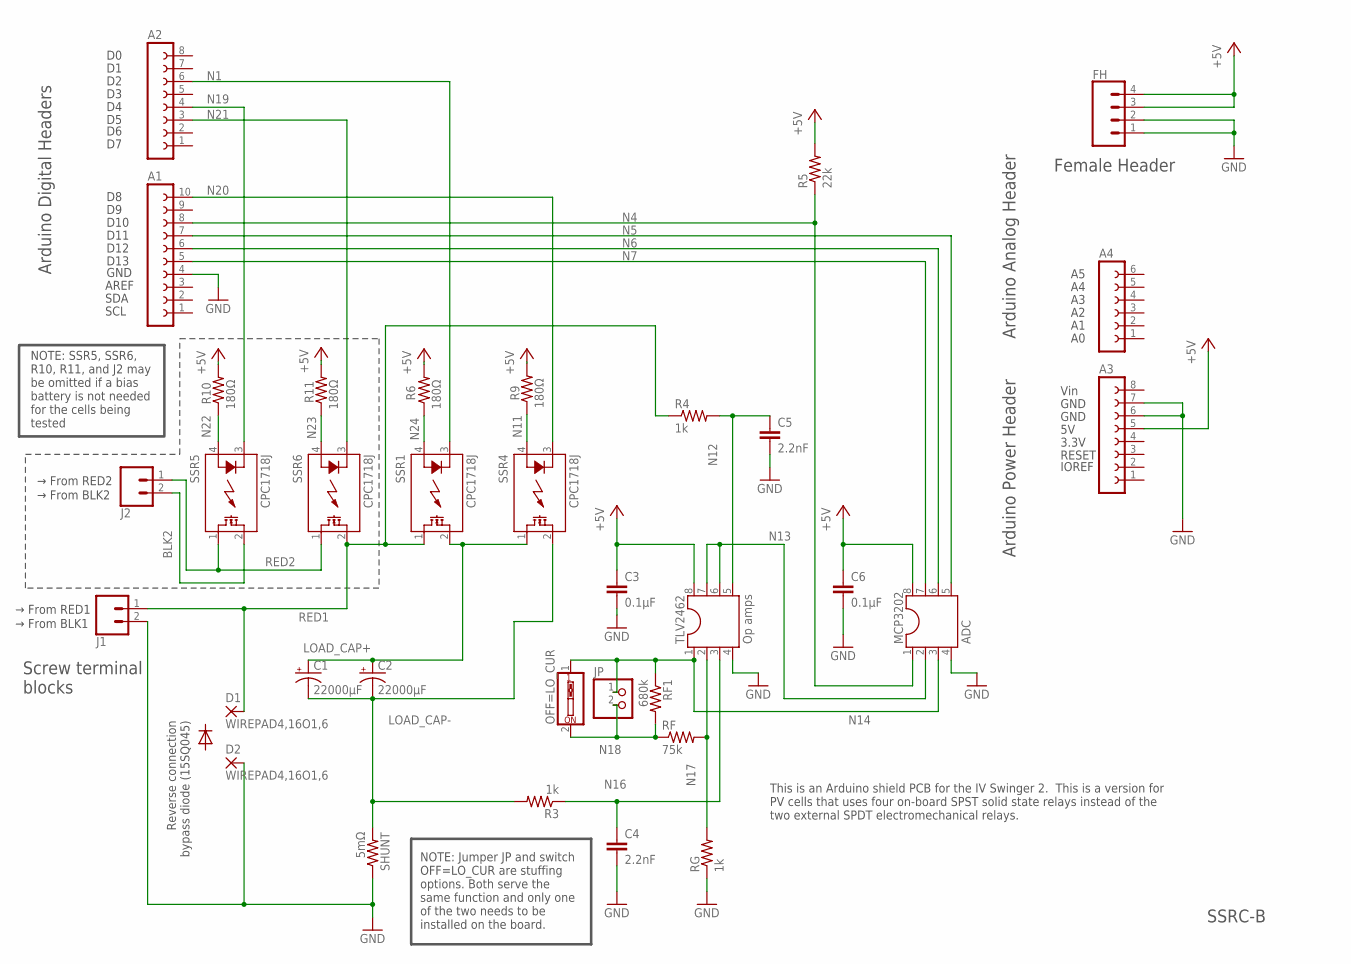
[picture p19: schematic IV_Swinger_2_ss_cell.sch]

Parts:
A1: FE10-1; FE10
A2, A3: FE08-1; FE08
A4: FE06-1; FE06
C1, C2: 22000µF; E7,5-18
C3, C6: 0.1µF; C025-030X050
C4, C5: 2.2nF; C025-030X050
D1, D2: WIREPAD4,16O1,6; 4,16O1,6
FH: CONN_04LONGPADS; 1X04_LONGPADS
J1, J2: CONN_025MM; SCREWTERMINAL-5MM-2
JP: PINHD-1X2; 1X02
MCP3202: ADC; SOCKET-08
OFF=LO_CUR: SW_DIP-1; EDG-01
R3, R4: 1k; 0207/10
R5: 22k; 0207/10
R6, R9, R10, R11: 180Ω; 0207/10
RF: 75k; 0207/10
RF1: 680k; 0207/10
RG: 1k; 0207/10
SHUNT: 5mΩ; 0617/17
SSR1, SSR4, SSR5, SSR6: CPC1718J; I4-PAC
TLV2462: Op amps; SOCKET-08

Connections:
+5V: A3.5, C3.1, C6.1, FH.3, FH.4, MCP3202.8, R5.2, R6.2, R9.2, R10.2, R11.2, TLV2462.8
BLK2: J2.2, SSR5.2 (DS2)
GND: A1.4, A3.6, A3.7, C3.2, C4.2, C5.2, C6.2, D2.1, FH.1, FH.2, J1.2, MCP3202.4, RG.1, SHUNT.1, TLV2462.4
LOAD_CAP+: C1.+, C2.+, SSR1.2 (DS2), SSR4.1 (DS1)
LOAD_CAP-: C1.-, C2.-, R3.2, SHUNT.2, SSR4.2 (DS2)
N1: A2.6, SSR1.3 (K)
N4: A1.8, MCP3202.1, R5.1
N5: A1.7, MCP3202.5
N6: A1.6, MCP3202.6
N7: A1.5, MCP3202.7
N11: R9.1, SSR4.4 (A)
N12: C5.1, R4.2, TLV2462.5
N13: MCP3202.2, TLV2462.6, TLV2462.7
N14: JP.1, MCP3202.3, OFF=LO_CUR.1, RF1.1, TLV2462.1
N16: C4.1, R3.1, TLV2462.3
N17: RF.2, RG.2, TLV2462.2
N18: JP.2, OFF=LO_CUR.2, RF.1, RF1.2
N19: A2.4, SSR5.3 (K)
N20: A1.10, SSR4.3 (K)
N21: A2.3, SSR6.3 (K)
N22: R10.1, SSR5.4 (A)
N23: R11.1, SSR6.4 (A)
N24: R6.1, SSR1.4 (A)
RED1: D1.1, J1.1, R4.1, SSR1.1 (DS1), SSR6.2 (DS2)
RED2: J2.1, SSR5.1 (DS1), SSR6.1 (DS1)

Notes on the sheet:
→ From BLK1
Screw terminal blocks
SCL
SDA
AREF
D13
D12
GND
D10
D11
RESET
3.3V
IOREF
Vin
Arduino Digital Headers
Arduino Analog Header
Arduino Power Header
Female Header
SSRC-B
This is an Arduino shield PCB for the IV Swinger 2. This is a version for PV cells that uses four on-board SPST solid state relays instead of the two external SPDT electromechanical relays.
→ From RED1
→ From BLK2
→ From RED2
NOTE: Jumper JP and switch OFF=LO_CUR are stuffing options. Both serve the same function and only one of the two needs to be installed on the board.
NOTE: SSR5, SSR6, R10, R11, and J2 may be omitted if a bias battery is not needed for the cells being tested
Reverse connection bypass diode (15SQ045)

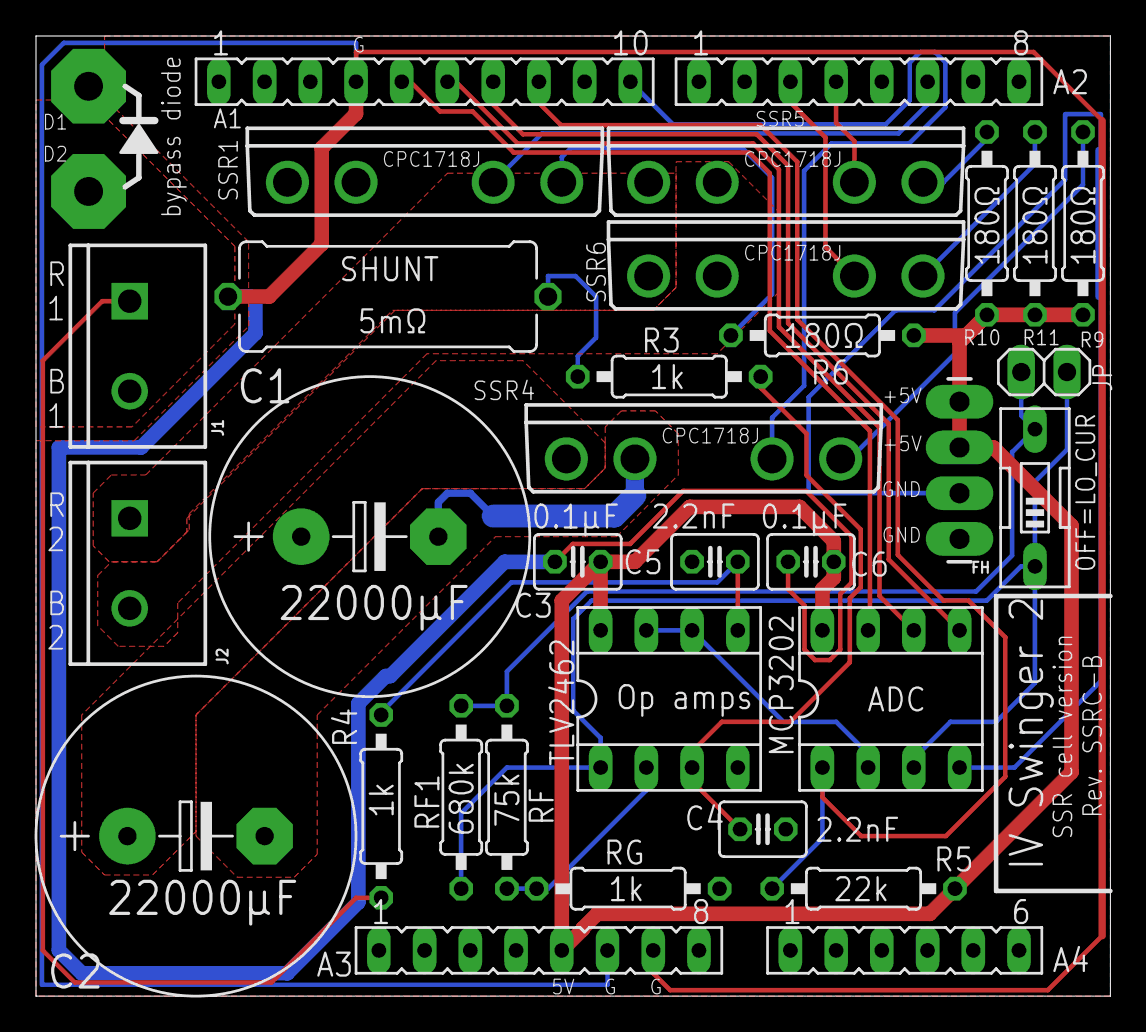
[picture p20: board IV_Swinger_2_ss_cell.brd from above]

Board: 2 copper layers, 59.7 x 53.3 mm, 34 parts (0 on the bottom side), 25 nets.

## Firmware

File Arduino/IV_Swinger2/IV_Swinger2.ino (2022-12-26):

/*
 *-----------------------------------------------------------------------------
 *
 * IV_Swinger2.ino: IV Swinger 2 Arduino sketch
 *
 * Copyright (C) 2017-2022  Chris Satterlee
 *
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
 *-----------------------------------------------------------------------------
 *
 * IV Swinger and IV Swinger 2 are open source hardware and software
 * projects
 *
 * Permission to use the hardware designs is granted under the terms of
 * the TAPR Open Hardware License Version 1.0 (May 25, 2007) -
 * http://www.tapr.org/OHL
 *
 * Permission to use the software is granted under the terms of the GNU
 * GPL v3 as noted above.
 *
 * Current versions of the licensing files, documentation, Fritzing file
 * (hardware description), and software can be found at:
 *
 *    https://github.com/csatt/IV_Swinger
 *
 *-----------------------------------------------------------------------------
 *
 * This file contains the Arduino sketch for the IV Swinger 2. It
 * performs the following functions:
 *
 *     - Participates in handshakes with the host computer (via USB)
 *     - Receives configuration options from the host
 *     - Communicates debug messages to the host
 *     - Controls the relay that switches the capacitor between the
 *       bleed circuit and the PV circuit
 *     - Reads and records values from the two ADC channels
 *     - Waits for current to stabilize at the beginning
 *     - Compensates for the fact that time passes between the current
 *       and voltage measurements
 *     - Selectively discards values so that the Arduino memory isn't
 *       exhausted before the IV curve is complete
 *     - Determines when the IV curve is complete
 *     - Sends results to the host
 *
 * Performance is important. The rate that the curve is "swung" is a
 * function of the capacitor value and the PV module; there is no way to
 * slow it down (other than using a larger capacitance).  The faster the
 * software can take measurements, the closer together the points will
 * be, which improves the "resolution" of the IV curve.  Because i = C *
 * dv/dt, the speed of the sweep is not constant from the Isc end of the
 * curve to the Voc end. It is faster (i.e. dt is smaller) when current
 * (i) is higher and when the voltage change (dv) between points is
 * lower. At the beginning of the curve, i is high, but dv is also high,
 * so the sweep speed is moderate. And at the end of the curve, both i
 * and dv are low, so the sweep speed is also moderate. But just past
 * the knee, i is still high but dv is low, so the sweep rate is the
 * highest. If the software performance is poor, this part of the curve
 * will have poor resolution.
 *
 * The downside of taking measurements quickly is that too many
 * measurements are taken during the parts of the curve where the sweep
 * rate is low. The Arduino has very limited memory, so if all these
 * points are recorded, memory will be exhausted before the curve is
 * complete. The software must selectively discard points to prevent
 * this from happening. The trick is to determine which points to
 * discard. It is not useful to have points that are very close to each
 * other, so the discard criterion is based on the distance between
 * points. This calculation has to be very fast because it is performed
 * after every measurement, and that reduces the rate that measurements
 * can be taken. Any use of floating point math, or even 32-bit (long)
 * math slows things down drastically, so only 16-bit integer math is
 * used. Instead of Pythagorean distance, so-called Manhattan distance
 * is used, which only requires subtraction and addition. The criterion
 * distance could be a constant, but that would not produce good results
 * for all IV curves. Instead, it is scaled based on the measured values
 * for Voc and Isc. The Voc values are read before the relay is
 * activated and the Isc values are determined just after the relay is
 * activated. The minimum distance criterion calculation requires some
 * computation time between the first two measured points, but that is
 * not normally a resolution-sensitive part of the curve. Nevertheless,
 * this code is also restricted to simple 16-bit integer math in order
 * to make it as quick as possible.
 *
 * A single point on the curve requires reading both channels of the
 * ADC. There is no way to read both values at the same time; each read
 * requires a separate SPI transaction, so some time passes between the
 * two reads, and the values do not represent the exact same point in
 * time. The simplest way to deal with this would be to ignore it; if
 * the points are close enough together, the effect is relatively
 * minor. But it isn't difficult to compensate for, so we do.  One way
 * to compensate would be to do three reads for each pair
 * (i.e. CH0/CH1/CH0 or CH1/CH0/CH1) and average the first and third.
 * But that would slow things down by 50%.  Instead, we just do one read
 * of each channel on each iteration, but interpolate between the CH1
 * values of each iteration. The catch is that there is computation
 * between iterations (which takes time), so it's not a simple average;
 * it's a weighted average based on measured times.
 *
 * Cell version support:
 *
 * The Arduino code does exactly the same thing for a cell version IVS2
 * as it does for the module version. There is, however, a configuration
 * command that the host software uses to turn on or turn off the second
 * relay.
 *
 * SSR support:
 *
 * This code supports both the original electromechanical relay (EMR)
 * designs and the more recent solid-state relay (SSR) designs.  The
 * code does not "know" which type of relay is in use. The EMR is an
 * SPDT switch, so only one is needed to switch between the bleed
 * circuit and the PV circuit.  SSRs are SPST, so two are required for
 * the same functionality (SSR1 and SSR2). A third SSR is needed because
 * of the slow turn-on time of SSR1 (7.5ms typical).  SSR3, when active,
 * bypasses the load capacitors.  SSR1 is controlled by the same Arduino
 * pin as the EMR (pin D2).  SSR2 is controlled by a different pin
 * (D6). SSR1 is turned on ("closed") and SSR2 is turned off ("opened")
 * after the Voc measurement has been taken - as usual.  SSR3,
 * controlled by Arduino pin D7, is turned on at this point as well
 * (actually just before). In this state, the PV current flows through
 * SSR1 and SSR3 and through the shunt.  The load capacitors do not
 * start charging yet, and the current has a very near short-circuit
 * path.  The Isc polling is started at this point. When the voltage and
 * current stop changing, SSR3 is turned off ("opened"), the load
 * capacitors start to charge, and the curve is traced.  When the curve
 * is complete, SSR1 is turned off, and SSR2 is turned on.  In this
 * state, the load capacitors drain through SSR2 and the bleed resistor.
 * The relays stay in this state until the next curve is swung. Since
 * nothing is connected to Arduino pins D6 and D7 in the EMR design,
 * there is no effect of the code that is controlling SSR2 and SSR3. And
 * since SSR1 activated (and SSR2 deactivated) at exactly the same times
 * as the EMR (using the same Arduino pin for SSR1), the code does the
 * right thing. [In a design without SSR3, the load capacitors would
 * start charging up while SSR1 is still turning on.  During the turn-on
 * period, SSR1 has a significant resistance. By the time it is fully
 * turned on, the load capacitors have a significant resistance.  There
 * is never a time when the PV "sees" anything close to a short circuit,
 * and the curve is truncated on the Isc end.  SSR3 provides a
 * short-circuit path around the load capacitors, keeping them from
 * charging until SSR1 is fully on.]
 *
 * The SSR cell version has four SSRs. SSR1 is the same as SSR1 in the
 * module version, connected to Arduino pin D2. There is no SSR2 or SSR3
 * in the cell version.  SSR4 takes the place of SSR2 and SSR3 and is
 * used both to bleed and to bypass the load capacitors since there is
 * no bleed resistor.  It is controlled by Arduino pin D8. SSR5 and SSR6
 * together provide the function of the second relay in the non-SSR cell
 * version. SSR5 is controlled by Arduino pin D4, just like the second
 * relay. SSR6 is controlled by Arduino pin D5.  As with the other SSRs,
 * the versions that do not have SSR4, SSR5, and SSR6 are not affected
 * when the pins controlling them are activated or deactivated since
 * nothing is connected to those pins in the other versions.
 *
 * FET support:
 *
 * This code also supports the even newer FET-based design (module
 * only). In place of SSR1, SSR2, and SSR3 are FET1, FET2, and FET3. The
 * FETs are activated and deactivated at the same times as their SSR
 * counterparts. The only difference is that FET3 is active-high,
 * whereas SSR3 is active-low. To make this work without the code having
 * to "know" which type the hardware is, FET3 is controlled by a
 * different Arduino digital output pin from SSR3 (D9 instead of
 * D7). Note that the "SSR" constant and variable names have not been
 * changed to reflect that they now actually mean "SSR or FET".
 * 
 */
#define VERSION "1.4.6"         // Version of this Arduino sketch

// Uncomment one or more of the following to enable the associated
// feature. Note, however, that enabling these features uses more of the
// Arduino's SRAM, so we have to reduce the maximum number of IV points
// accordingly to prevent running out of memory.
//#define DS18B20_SUPPORTED
//#define ADS1115_PYRANOMETER_SUPPORTED
//#define CAPTURE_UNFILTERED_ISC_POLL     // Debug only
//#define CAPTURE_UNFILTERED_POST_ISC     // Debug only

#if defined(CAPTURE_UNFILTERED_ISC_POLL) || \
    defined(CAPTURE_UNFILTERED_POST_ISC)
#define CAPTURE_UNFILTERED
#endif

#include <SPI.h>
#include <EEPROM.h>

#ifdef DS18B20_SUPPORTED
#include <OneWire.h>
#include <DallasTemperature.h>
#define DS18B20_SRAM 44
#else
#define DS18B20_SRAM 0
#endif

#ifdef ADS1115_PYRANOMETER_SUPPORTED
#include <Wire.h>
#include <Adafruit_ADS1015.h>
#define ADS1115_SRAM 224
#define ADS1115_IRRADIANCE_POLLING_LOOPS 10
#define ADS1115_TEMP_POLLING_LOOPS 5
#define MAX_STABLE_TEMP_ERR_PPM 5000    // 5000 = 0.5%
#define MAX_STABLE_IRRAD_ERR_PPM 10000  // 10000 = 1%
#else
#define ADS1115_SRAM 0
#endif

#ifdef CAPTURE_UNFILTERED
#define MAX_UNFILTERED_POINTS 125
#define UNFILTERED_SRAM ((MAX_UNFILTERED_POINTS*4)+12)
#else
#define UNFILTERED_SRAM 0
#endif
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

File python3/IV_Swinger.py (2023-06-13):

#!/usr/bin/env python
"""IV Swinger control module"""
# pylint: disable=too-many-lines
#
###############################################################################
#
# IV_Swinger.py: IV Swinger control module
#
# Copyright (C) 2016-2023  Chris Satterlee
#
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
###############################################################################
#
# The IV Swinger is an open source hardware and software project
#
# Permission to use the hardware design is granted under the terms of
# the TAPR Open Hardware License Version 1.0 (May 25, 2007) -
# http://www.tapr.org/OHL
#
# Permission to use the software is granted under the terms of the GNU
# GPL v3 as noted above.
#
# Current versions of the licensing files, documentation, hardware
# design files, and software can be found at:
#
#    https://github.com/csatt/IV_Swinger
#
###############################################################################
#
# NOTE: This module was originally written for IV Swinger 1. The
# remainder of this comment block pertains to IV Swinger 1. Much of the
# code in this module is specific to IV Swinger 1 and is not used for IV
# Swinger 2. On the other hand, a lot of the code was applicable to IV
# Swinger 2, so it was re-used as much as possible. The comment '# IVS1'
# identifies code that is not used at all for IV Swinger 2, and that
# comment is used when running code coverage to exclude the
# IVS1-specific code from the coverage metrics.
#
###############################################################################
#
# This file contains the Python code that controls the IV Swinger
# hardware, captures measurements, and displays the results graphically.
#
# The hardware consists of a chain of loads that are selected or
# deselected using relays.  When a load is deselected, the current
# passes through a wire bypassing that load.  Ideally when all loads are
# deselected, the resistance of the chain would be zero (short circuit).
# In reality the bypass wires, relay terminal connections, and relay
# contacts have small resistances that add up to a non-negligible total
# (close to half an ohm).
#
# There are 16 relays (two 8-relay Sainsmart-type modules) which are
# driven by a MCP23017 I/O extender IC that is controlled from the
# Raspberry Pi i2c bus.  The MCP23017 outputs are connected to the
# relays as follows.  This list in is order from RIGHT to LEFT as seen
# from the front of the box.
#
# MCP23017  Relay pin         Load (see defines below)
# --------  ---------         ----
#  B0       Module 1, IN1     HALF
#  B1       Module 1, IN2     OPEN
#  B2       Module 1, IN3     ONE
#  B3       Module 1, IN4     TWO
#  B4       Module 1, IN5     THREE
#  B5       Module 1, IN6     FOUR
#  B6       Module 1, IN7     FIVE
#  B7       Module 1, IN8     SIX
#  A7       Module 0, IN1     SEVEN
#  A6       Module 0, IN2     EIGHT
#  A5       Module 0, IN3     NINE
#  A4       Module 0, IN4     TEN
#  A3       Module 0, IN5     ELEVEN
#  A2       Module 0, IN6     TWELVE
#  A1       Module 0, IN7     THIRTEEN
#  A0       Module 0, IN8     FOURTEEN
#
# Note that one of the "loads" (OPEN) is actually not connected.  This
# was a design change required to support maximizing the lifetime of the
# relay contacts. The load bank does include a coil associated with this
# relay, but one of its leads is simply left unconnected so that when
# the relay is activated the circuit is open. The OPEN load is in the
# second position purely for logistical reasons; it was the easiest one
# to disconnect when the decision was made to implement the change.
#
# There is a double-pole single-throw (DPST) switch in the load circuit
# that has two purposes: 1) on one side it opens and closes the load
# circuit, and 2) on the other side it is connected to a GPIO pin so the
# code can sense whether the load circuit is open or closed and can poll
# for changes.  While the load circuit is open, the code continuously
# measures the voltage and records the last value before it detects that
# the switch was flipped - this is the Voc value.  Then it starts into a
# loop of incrementally adding to the load value and at each increment
# measuring and recording the current (I) and the voltage (V).
#
# The ADS1115 analog-to-digital converter (ADC) is used for both the
# voltage and current measurements.  The ADS1115 is also controlled and
# read via the Raspberry Pi i2c bus.  Since the voltage generated by a
# PV panel can be much higher than the 5V maximum ADC input voltage, the
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

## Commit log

2015-12-04 Initial population of repository
    - Added directories: docs, Fritzing, python
    - Added respective files to these directories
    - Added LICENSE file to each directory: docs and Fritzing get the TAPR
    Open Hardware License; python gets GNU GPL v.3
    - Replaced top-level LICENSE file with text describing this
    [IV_Swinger.fzz, IV_Swinger_BOM.xlsx]
2016-04-14 Major code refactoring
    - Converted to full OOP, importable design
    - Added better handling of some cases that had caused crashes (Isc=0,
    USB errors)
    - Eliminated global variables
    - Added shutdown on exceptions
    - Added handling of exceptions in threads
    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
2016-04-28 Switch to matplotlib, add plotter utility
    This change adds the IV_Swinger_plotter utility. It is a CLI tool that
    allows the user to re-generate PDF plots from CSV data point files from
    previous runs. It supports overlaying multiple curves on the same
    graph, plotting the power curve with the IV curve, and many other
    customization options. It can be run on a Mac or any other platform
    that has the necessary Python support. Installing gnuplot on a Mac is a
    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
2017-04-24 IV Swinger 2 User Guide, etc
    Added IV_Swinger1 and IV_Swinger2 folders under docs. Moved all
    existing docs to IV_Swinger1 folder. Added IV Swinger 2 User Guide
    (Word and PDF) to IV_Swinger2 folder.
    Updated README.md to announce IV Swinger 2 and link to new demo videos.
    [IV_Swinger_BOM.xlsx]
2017-04-26 Added IV Swinger 2 Fritzing files
    Added IV_Swinger2.fzz Fritzing file. Also added PDFs of the breadboard
    and schematic views to the Fritzing folder.
    [IV_Swinger2.fzz]
2017-04-26 Added BOM spreadsheet
    Added IV_Swinger2_BOM.xlsx. Also changed $35 cost estimate in User
    Guide to $50.
    [IV_Swinger2_BOM.xlsx]
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2017-05-03 Update IVS2 Fritzing files
    Somehow I previously committed an older version of the Fritzing file
    and the two PDFs. This corrects that mistake.
    [IV_Swinger2.fzz]
2017-05-17 Minor corrections to BOM SS and step-by-step instructions
    Added jumper wires to the BOM. Made minor corrections and
    clarifications to step-by-step instructions.
    [IV_Swinger2_BOM.xlsx]
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2018-07-02 Cell version Fritzing files
    Fritzing design for the IVS2 cell version, plus:
    - Cell version breadboard PDF
    - Cell version schematic PDF
    - GIF that flips between module and cell breadboard view
    - GIF that flips between module and cell schematic view
    [IV_Swinger2_cell.fzz]
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2018-07-10 Add BOM spreadsheet for cell version
    Copy of BOM spreadsheet for module IVS2, but with changes for cell version in large red font (and grayed out for items not needed)
    [IV_Swinger2_Cell_Version_BOM.xlsx]
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2018-09-20 First cut at EAGLE PCB
    Added PCB directory, and under that, EAGLE directory.
    First cut at an Arduino shield for the module version IVS2.
    [IV_Swinger_2_module.brd, IV_Swinger_2_module.sch]
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2018-10-19 PCB reorg + add SSR version
    Reorganized PCB files so board type is at the top level, and each has EAGLE and Gerber folders under it.
    README file has description of each one, plus status and ordering info.
    Added files for the SSR version.
    [IV_Swinger_2_module.brd, IV_Swinger_2_module.sch, IV_Swinger_2_ss_mod.brd, IV_Swinger_2_ss_mod.sch]
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2018-12-11 SSR module version PCB, RevB
    Fixed bugs in RevA of the SSR module version PCB:
    Issue #40: Must drive SSR1 and SSR2 from separate Arduino pins. In the RevA design, there is a path from +5V to GND through the two SSRs, which can cause destruction of the SSRs and the bleed resisto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
    Issue #41: Resistor R3 must be connected precisely to the shunt (+) end pad so it doesn't see the voltage at some point in the sea of copper that is the LOAD_CAP- net. This resulted in current measur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
    Issue #41: The path from the shunt (-) end pad to the screw terminal pads must be a stub off the GND plane s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
    [IV_Swinger_2_ss_mod.brd, IV_Swinger_2_ss_mod.sch]
2018-12-18 Standard (EMR-based) PCB update to RevB
    This is RevB of the standard IVS2 EMR-based module version PCB. It is based on RevB of the SSR-based module version. The main purpose of this revision is to make the SSR and EMR versions as similar a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
    - the connections to the binding posts are both on a screw-terminal block on the left end of the board (like SSR version)
    - pads are provided for the bypass diodes (like SSR version)
    - the current-carrying path from the shunt is now isolated in a stub off the ground plane (like SSR version)
    - R3 is now connected to the shunt with a dedicated trace (like SSR version)
    - Connections to EMR are from a second screw-terminal bl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
    [IV_Swinger_2_module.brd, IV_Swinger_2_module.sch]
2019-01-06 Cosmetic changes to EMR module PCB files
    One extremely small change to .brd file and several minor changes to .sch file to sync with other versions. No functional difference: still RevB
    [IV_Swinger_2_module.brd, IV_Swinger_2_module.sch]
2019-01-06 Cell version PCB files
    This commit contains the EAGLE files and Gerber zip for the standard EMR-based cell version PCB.
    [IV_Swinger_2_cell.brd, IV_Swinger_2_cell.sch]
2019-01-06 SSR cell version PCB files
    This commit contains the EAGLE files and Gerber zip for the SSR-based cell version PCB.
    [IV_Swinger_2_ss_cell.brd, IV_Swinger_2_ss_cell.sch]
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2019-01-10 Add PCB BOMs
    Add configurable spreadsheet for bills-of-material for all four PCB variants.
    Also, PDFs for each of the four.
    Also, GIFs for pairwise comparisons.
    [IV_Swinger_2_PCB_BOM.xlsx]
2019-01-10 Minor BOM fixes/changes
    Changed IC sockets from Amazon to Digi-Key
    Add bias battery holders and D-cells for cell version
    Fix some cosmetic issues
    [IV_Swinger_2_PCB_BOM.xlsx]
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2019-02-01 Move Perma-Proto construction docs into a subfolder
    Create new Perma_Proto_construction folder under docs/IV_Swinger2 and move all Perma-Proto construction documents into that folder. There will be a new PCB_construction folder for the PCB constructio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
    [IV_Swinger2_BOM.xlsx, IV_Swinger2_Cell_Version_BOM.xlsx]
2019-02-01 Update PCB BOMs
    Minor changes and fixes to the master BOM. PDFs and GIFs regenerated too.
    [IV_Swinger_2_PCB_BOM.xlsx]
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2019-02-07 Change SSR4 from lin D1 to D8 on SSR cell version PCB (Issue #49)
    This fixes Issue #49 on the SSR cell version PCB. SSR4 is now controlled by Arduino pin D8. This is now RevB (or SSRC-B) of this PCB.
    This commit includes:
    EAGLE files, .sch and .brd
    Zip of the Rev_B Gerber files
    PDFs of the modified schematic, and the modified top and bottom images
    Updated GIFs that compare the SSR cell version with the other variants
    [IV_Swinger_2_ss_cell.brd, IV_Swinger_2_ss_cell.sch]
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2022-01-27 New files for FET version (Issue #179)
    Add initial versions of FET version PCB files, BOM, and step-by-step instructions
    [IV_Swinger_2_fet_mod.brd, IV_Swinger_2_fet_mod.sch, fet_mod_DigiKey_Mouser.csv]
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2022-02-27 Update files for EMR module Instructable
    Updated the step-by-step doc and BOMs for the EMR module version. Mostly add alternate parts.
    [emr_mod_DigiKey_Mouser.csv]
2022-02-28 Update files for SSR module Instructable
    Updated the step-by-step doc and BOMs for the SSR module version. Mostly add alternate parts.
    [ssr_mod_DigiKey_Mouser.csv]
2022-02-28 Update files for EMR cell Instructable
    Updated the step-by-step doc and BOMs for the EMR cell version. Mostly add alternate parts.
    [emr_cell_DigiKey_Mouser.csv]
2022-02-28 Update files for SSR cell Instructable
    Updated the step-by-step doc and BOMs for the SSR cell version. Mostly add alternate parts.
    Note that the Instructable itself has not bee created and probably never will be.
    [ssr_cell_DigiKey_Mouser.csv]
2022-02-28 Update master PCB BOM spreadsheet
    Add support for FET and update Digi-Key links
    [IV_Swinger_2_PCB_BOM.xlsx]
2022-03-01 Update files for original (Perma-Proto) Instructable
    Updated the step-by-step doc and BOMs for the Perma-Proto version. Adds info on FET version in Step 1. BOM has updated Digi-Key link with alternate parts.
    [IV_Swinger2_BOM.xlsx, PermaProto_Digikey_Mouser.csv]
2022-03-01 Updated BOM file for PermaProto cell version
    There is no Instructable for this version, but the BOM spreadsheet is updated for alternate parts
    [IV_Swinger2_Cell_Version_BOM.xlsx]
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2023-04-03 Fix some BOM part numbers
    I made these changes four months ago but didn't commit. The DIP sockets had an incorrect part Mouser number (8-pin instead of 4-pin).
    [emr_cell_DigiKey_Mouser.csv, emr_mod_DigiKey_Mouser.csv, fet_mod_DigiKey_Mouser.csv, ssr_cell_DigiKey_Mouser.csv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]
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2025-03-13 Correct EAGLE files for FET module version (Issue #218)
    Replace the incorrect files with the correct ones.
    [IV_Swinger_2_fet_mod.brd, IV_Swinger_2_fet_mod.sch]

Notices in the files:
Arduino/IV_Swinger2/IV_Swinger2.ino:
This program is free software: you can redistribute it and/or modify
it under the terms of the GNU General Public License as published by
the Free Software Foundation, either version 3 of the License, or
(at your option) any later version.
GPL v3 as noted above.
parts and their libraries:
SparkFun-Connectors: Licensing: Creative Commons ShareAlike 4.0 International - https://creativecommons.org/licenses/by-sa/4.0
